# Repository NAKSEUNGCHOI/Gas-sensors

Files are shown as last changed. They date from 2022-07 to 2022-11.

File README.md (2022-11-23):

# Project Gas(Air quality) sensors

* University of Washington Summer 2022 
* Prof. Vikram Iyer.
* Nakseung Choi | graduate research assistant @ SSOL UW 

## Description

* Prof. Vikram Iyer and I are currently building low power low cost gas sensors (CO2, CO, and black carbon) to help two groups of scientists collect data for their research studies. One group wants to get data in the greater Seattle area to study on where these gasses are coming from. Ultimately, they would like to expand the number of the gas sensors in different locations such that they can compare with other locations for further studies.
The other group would like to place these gas sensors in the middle of moutains in the eastern Washington to study how these gases(CO2 and CO) affect wild animals when there is an unexpected wildfire going. 

* We are currently testing several CO2 sensors to compare their functionality with a commercial device. In the mean time, we just got done with our own PCB design for SPEC CO sensor as well as hardware/software integration. Depending on how precise data the scientists need, we are going to make it acordingly. nRF52480 Arm Cortex-m4 is probably going to be used for the MCU. Using Lora radio communication, a long distance communication interface will also be implemented to update data to the web server such that the scientists can check the data in real time.  

## Authors

- Nakseung Choi
- Please check out my Linkedin: https://www.linkedin.com/in/nakseung-choi-090a1b69/

## Release Notes

* <pre> New Tube arrived. About to go install the MA350 on the rooftop                       11-22-2022</pre>
* <pre> 300ml/min 60 ml/min for 5 wavelengths tests are done. missing 60 ml/min with UV+IR    9-12-2022</pre>
* <pre> Created another python code to draw different plots for CO2 sensors                   9-12-2022</pre>
* <pre> Wrote a python code to plot CO2 sensors - avg of two aranets for 4 sensors            9-08-2022</pre>
* <pre> wrote a python program using mathplot to graph the CO2 data  (Still testing MA350)    9-07-2022</pre>
* <pre> Testing the MA350                                                                     8-29-2022</pre>
* <pre> arduino / python serial communication script complete. Sending data to adafruitIO     8-26-2022</pre>
* <pre> presentation done. more CO testing / preparing to set up MA350.                       8-24-2022</pre>                                                
* <pre> got the CO sensor working with noise. more testing...........                         8-23-2022</pre>
* <pre> created a new PCB board and testing..                                                 8-22-2022</pre>
* <pre> presentation preparation2                                                             8-20-2022</pre>
* <pre> presentation preparation                                                              8-20-2022</pre>
* <pre> Software done. software/hardware integration started                                  8-18-2022</pre>
* <pre> Testing CO sensor 2                                                                   8-17-2022</pre>
* <pre> Testing CO sensor                                                                     8-16-2022</pre>
* <pre> setting up Black Carbon sensor & CO sensor                                            8-15-2022</pre>
* <pre> testing two SCD41s, two aranets, two PASCO2s all together.                            8-15-2022</pre>
* <pre>Debugging Complete. Ready to go for a testing.                                         8-14-2022</pre>
* <pre>Debugging...                                                                           8-12-2022</pre>
* <pre>PASCO2s are going to be tested with scd41 and aranet4 together for the functionality   8-11-2022</pre>
* <pre>Xensiv PAS CO2 coding in python complete.                                              8-11-2022</pre>
* <pre>Xensiv PAS CO2 working. Testing started.                                               8-10-2022</pre>
* <pre>Debugging Xensiv PAS CO2                                                               8-09-2022</pre>
* <pre>Testing Xensiv PAS CO2 manufactured by Infineon.                                       8-08-2022</pre>
* <pre>All parts are done soldering onto the board. Going to test the PCB.                    8-07-2022</pre>
* <pre>CO sensor PCB design complete. About to sorder the CO sensor circuit.                  8-03-2022</pre> 
* <pre>Designing a new circuit for CO sensor due to the chip shortage (LMP9100 out of stock)  8-02-2022</pre>
* <pre>Installed CO2 sensor's in an office with two people.                                   7-28-2022</pre>
* <pre>CO Sensor PCB Design V2 complete.                                                      7-28-2022</pre>
* <pre>CO Sensor PCB Design complete.                                                         7-27-2022</pre>
* <pre>Testing 24 hours success.                                                              7-26-2022</pre>
* <pre>Testing two SCD41s and two aranets4s on Raspberry pi 3.                                7-25-2022</pre>
* <pre>Working on PCB design for CO sensor                                                    7-24-2022</pre>
* <pre>Implemented two SCD41s and two aranet4s on Raspberry pi 3 for a testing.               7-21-2022</pre>
* <pre>Implemented SCD41 on nRF52480 express with Lora Radio (RFM9x)                          7-07-2022</pre>
* <pre>Implemented SCD41 (via I2C) and Aranet4 (via Bluetooth) on Raspberry pi 3 (B type)     7-01-2022</pre>
* <pre>Started                                                                                6/24/2022</pre>

## License

Copyright @ Nakseung Choi.

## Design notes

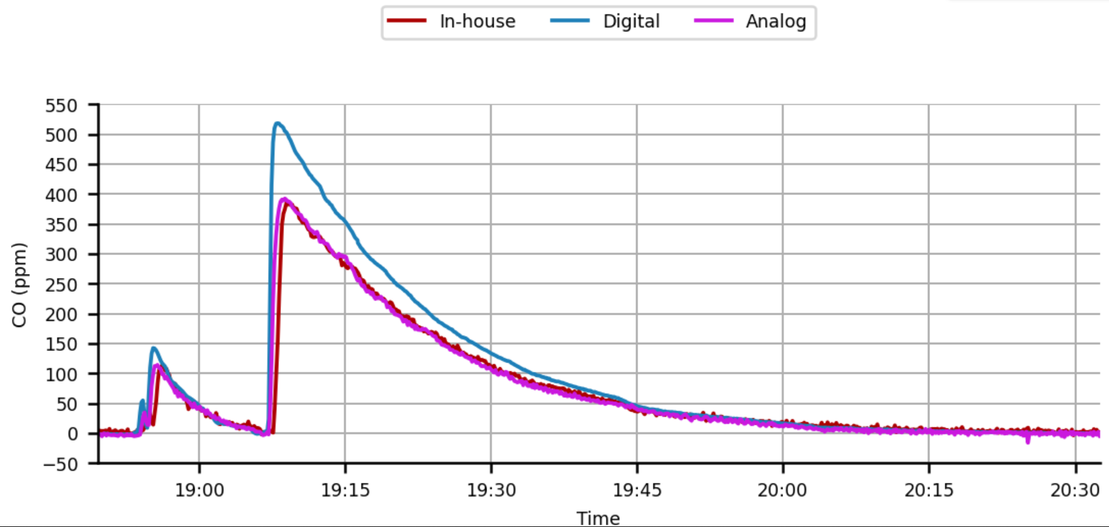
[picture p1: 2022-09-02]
CO/plot/CO_plot1.png

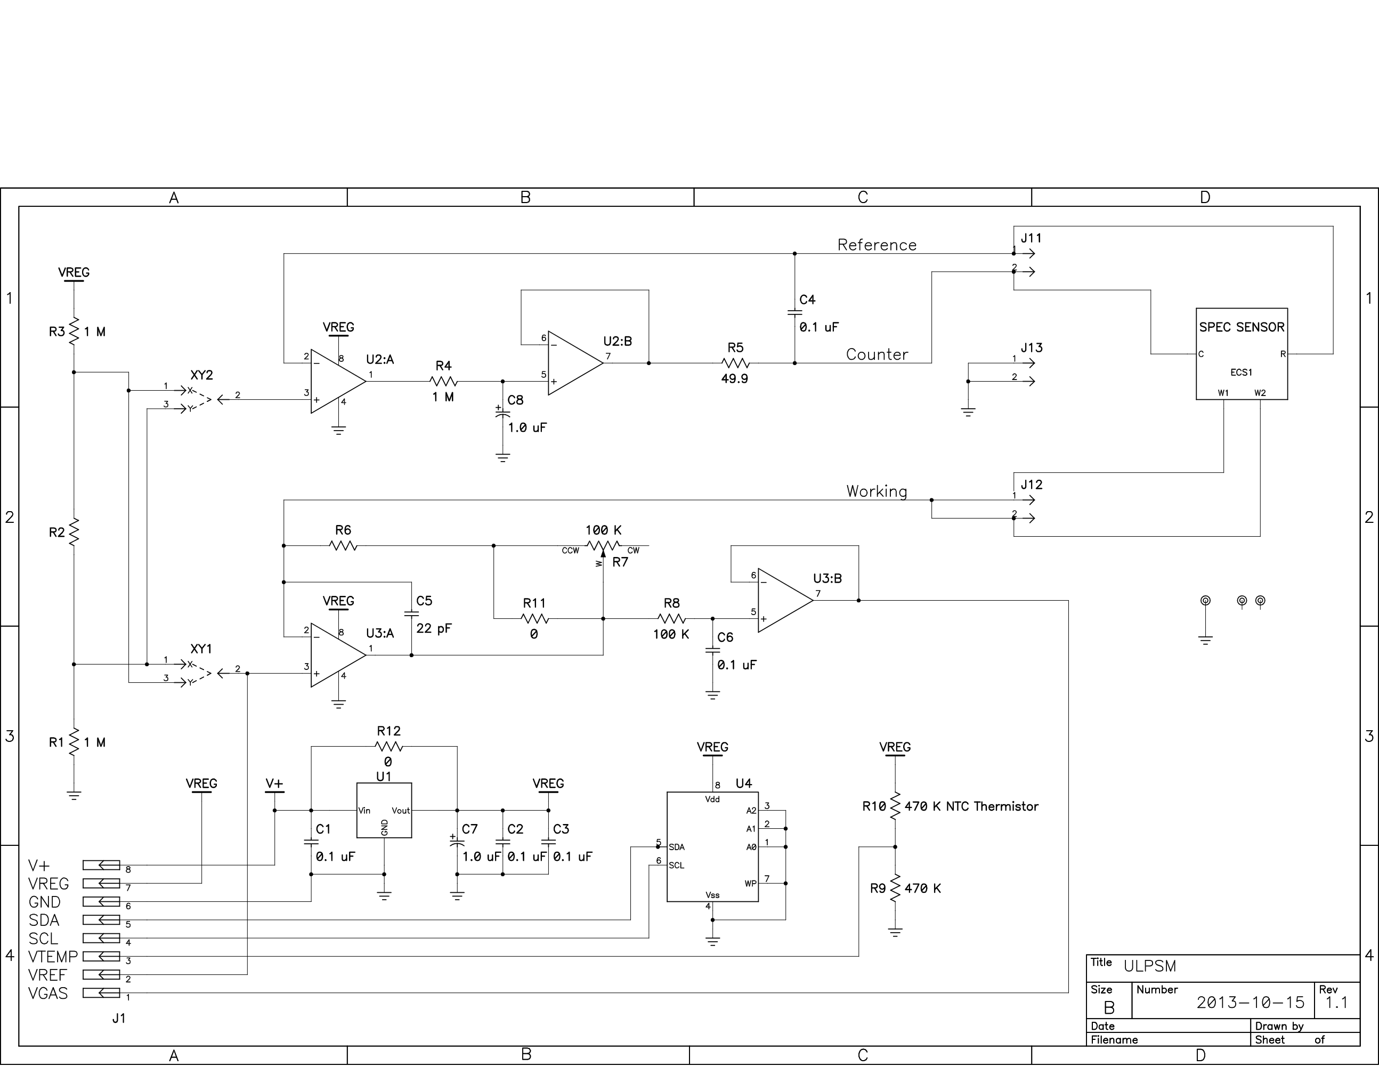
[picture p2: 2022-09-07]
CO/download.png

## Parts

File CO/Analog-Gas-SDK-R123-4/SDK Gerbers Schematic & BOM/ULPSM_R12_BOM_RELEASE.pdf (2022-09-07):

Bill of Materials | ULPSM Rev. 1.2
ULPSM | BOM Rev. 1.1
Item | Ref. Des. | # Req | Mfr.'s Part No. | Notes
Circuit Board | | 1 | ULPSM_R12
Connector, 8 pin female | J1 | 1 | Sullins PPPC081LGBN-RC
Capacitor, Ceramic, 0.1uF 25V SMT0805 | C1-4, 6 | 1 | Kemet C0805C104K3RACTU
Capacitor, Ceramic, 22pF 50V SMT0805 | C5 | 1 | Kemet C0805C220K5GACTU
Capacitor, Ceramic, 1.0uF 25V SMT0805 | C7,8 | 2 | F951E105MPAAQ2
Resistor, 0.0 SMT0603 | BIAS +/- | 2 | Yageo RC0603JR-070RL | See ULPSM_R12 SETTINGS_TABLE
Resistor, 0.0 SMT0805 | R11,R12 | 2 | Yageo RC0805JR-070RL
Resistor, 1M 1% SMT0805 | R1,3,4 | 3 | Yageo RC0805FR-071ML
Resistor, Variable Value, 1% SMT0805 | R2 | 1 | Variable Value | See ULPSM_R12 SETTINGS_TABLE
Resistor, 49.9 1% SMT0805 | R5 | 1 | Yageo RC0805FR-0749R9L
Resistor, Variable Value, 1% SMT0805 | R6 | 1 | Variable Value | See ULPSM_R12 SETTINGS_TABLE
Resistor, 100K 1% SMT0805 | R8 | 1 | Yageo RC0805FR-07100KL
Amplifier, dual, MSOP-8 pkg. | U2,U3 | 2 | Microchip MCP6042T-I/MS
Thermistor, 470K 5% NTC SMT0603 | R10 | 1 | MuRata NCP18WM474J03RB
Resistor, 470K 1% SMT0603 | R9 | 1 | Yageo RC0603FR-07470KL
Connector, 2 pin, female | J11-13 | 3 | 3M 950502-6102-AR
Captive Fastener/Standoff | HOLE | 1 | Captive Fastener CKFSE-116-4
IC, EEPROM, 16KBIT, MSOP-8 | U4 | 1 | Microchip 24AA16-I/MS | DNI
Voltage Regulator, 3V, SOT-23-5 | U1 | 1 | Seiko S-812C30AMC-C2KT2G | DNI
Potentiometer, 100K | R7 | 1 | Copal ST4ETB104 | DNI

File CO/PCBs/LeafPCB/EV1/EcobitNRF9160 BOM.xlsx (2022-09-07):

Column1 | Column2 | Column3 | Column4 | Column5 | Column6 | Column7 | Column8 | Column9
Part | Value | Device | Package | Description
BATT | 3-6VDC | CON_JST_PH_2PIN | JSTPH2 | JST 2-Pin Right-Angle Connector | https://www.digikey.com/product-detail/en/jst-sales-america-inc/S2B-PH-SM4-TB(LF)(SN)/455-1749-1-ND/926846 | 0.4194 | 1 | 0.4194
C1 | 10uF | CAP0402 | C-0402 | CAP | https://www.digikey.com/product-detail/en/murata-electronics-north-america/GRM155R60G106ME44D/490-10693-1-ND/5251412 | 0.011 | 1 | 0.011
C2, C3, C4, C5 | 1uF | CAPACITOR_0402_N | RESC0402_N | Generic chip capacitor | https://www.digikey.com/product-detail/en/samsung-electro-mechanics/CL05A105MQ5NNNC/1276-1235-1-ND/3889321 | 0.073 | 4 | 0.292
CHG |  | LED0805_NOOUTLINE | CHIPLED_0805_NOOUTLINE | LED | https://www.digikey.com/product-detail/en/lite-on-inc/LTST-C170AKT/160-1177-6-ND/1888608 | 0.1462 | 1 | 0.1462
JP1 | USB-RECEPTABLE | USB-RECEPTABLE | FCI-10103594-0001LF | USB Receptable | https://www.digikey.com/product-detail/en/amphenol-icc-fci/10103594-0001LF/609-4050-1-ND/2350357 | 0.5982 | 1 | 0.5982
L1 | 22nH | INDUCTOR_0603_N | RESC0603_N | Generic chip inductor | https://www.digikey.com/product-detail/en/johanson-technology-inc/L-14C22NJV4T/712-1438-1-ND/1914888 | 0.0438 | 1 | 0.0438
P1 | SF72S006VBAR2500 | SF72S006VBAR2500 | JAE_SF72S006VBAR2500 | SF72 series, nano-SIM card connector, normail open type, 6 connector | https://www.digikey.com/product-detail/en/SF72S006VBAR2500/670-2799-1-ND/5247732/?itemSeq=285035164 | 1.62 | 1 | 1.62
Q1 | Btn | SWITCH_TACT_SMT4.6X2.8 | BTN_KMR2_4.6X2.8 | SMT Tact Switches | https://www.digikey.com/product-detail/en/c-k/KMR231NG-LFS/CKN10246CT-ND/2176497 | 0.4065 | 1 | 0.4065
R1, R2, R4, R5, R6, R7 | 10k | RESR0402 | R0402 | RES | https://www.digikey.com/product-detail/en/susumu/RR0510P-103-D/RR05P10.0KDCT-ND/432960 | 0.0299 | 6 | 0.1794
R3 | 1k | RESR0402 | R0402 | RES | https://www.digikey.com/product-detail/en/susumu/RR0510P-102-D/RR05P1.0KDCT-ND/432937 | 0.0299 | 1 | 0.0299
THERM | 10k | RESISTOR_0402 | _0402 | Resistors | https://www.digikey.com/product-detail/en/susumu/RR0510P-103-D/RR05P10.0KDCT-ND/432960 | 0.0299 | 1 | 0.0299
U1 | ALS-PT19-315C | LIGHT_ALS-PT19-315C | ALS-PT19-315C | ALS-PT19-315C - Analog Light Sensor | https://www.digikey.com/product-detail/en/everlight-electronics-co-ltd/ALS-PT19-315C-L177-TR8/1080-1244-1-ND/2675978 | 0.2297 | 1 | 0.2297
U2 | NCP718 | NCP718 | NCP718-WDFN6 |  | https://www.digikey.com/product-detail/en/on-semiconductor/NCP718AMTADJTBG/NCP718AMTADJTBGOSCT-ND/9169230 | 0.3909 | 1 | 0.3909
U3 | MCP73831T-2ACI/OT | MCP73831/2 | SOT23-5 | MCP73831/2 LIPO Charger | https://www.digikey.com/product-detail/en/microchip-technology/MCP73831T-2ACI-OT/MCP73831T-2ACI-OTCT-ND/1979802 | 0.4326 | 1 | 0.4326
U4 | AP3418 | AP3418 | SOT25 |  | https://www.digikey.com/product-detail/en/diodes-incorporated/AP3418KTR-G1/AP3418KTR-G1DICT-ND/4505309 | 0.3399 | 1 | 0.3399
U5 | TPS22860DBVR | TPS22860DBVR | R-PDSO-G6 | Power Switch ICs - Power Distribution TPS22860 Ultra-low leakage load switch 6-SOT-23 -40 to 85 | https://www.digikey.com/product-detail/en/texas-instruments/TPS22860DBVR/296-43982-1-ND/5973206 | 0.5828 | 1 | 0.5828
 |  |  |  |  |  |  |  | 5.7522

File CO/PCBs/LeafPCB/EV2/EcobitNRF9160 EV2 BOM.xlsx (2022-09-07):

Column1 | Column2 | Column3 | Column4
Part | Value | Device | Package
ADC-CO | LMP91000SD/NOPB | LMP91000SD/NOPB | SON50P400X400X80-15N
ADC-NO2 | LMP91000SD/NOPB | LMP91000SD/NOPB | SON50P400X400X80-15N
ADC-O3 | LMP91000SD/NOPB | LMP91000SD/NOPB | SON50P400X400X80-15N
ADC-SO2 | LMP91000SD/NOPB | LMP91000SD/NOPB | SON50P400X400X80-15N
BATT | 3-6VDC | CON_JST_PH_2PIN | JSTPH2
C1 | 10uF | CAP0402 | C-0402
C2, C3, C4, C5, C6 | 1uF | CAPACITOR_0402_N | RESC0402_N
C7 | 10uF 10V 20% Tant | CAPACITOR_0805_N | RESC0805_N
C10, C11, C20, C30, C40 | 0.1uF | CAPACITOR_0603_N | RESC0603_N
CHG |  | LED0805_NOOUTLINE | CHIPLED_0805_NOOUTLINE
IC1 | ISL60002DIH320Z-TK | ISL60002DIH320Z-TK | SOT-23-3
JP1 | USB-RECEPTABLE | USB-RECEPTABLE | FCI-10103594-0001LF
L1 | 22nH | INDUCTOR_0603_N | RESC0603_N
P1 | SF72S006VBAR2500 | SF72S006VBAR2500 | JAE_SF72S006VBAR2500
Q1 | Btn | SWITCH_TACT_SMT4.6X2.8 | BTN_KMR2_4.6X2.8
R1, R4, R5, R6 | 10k | RESR0402 | R0402
R2 | 2M | R-US_R0603 | R0603
R3, R7 | 1k | RESR0402 | R0402
R11, R21, R31, R41 | 499k | RESISTOR_0603_N | RESC0603_N
R8 | 806k | R-US_R0603 | R0603
R10, R20, R30, R40 | 49.9k | RESISTOR_0603_N | RESC0603_N
IC2 | HDC1080 | HDC1080 | TI-S-PWSON-N6
U1 | VEML7700-TR | VEML7700-TR | XDCR_VEML7700-TR
U2 | NCP718 | NCP718 | NCP718-WDFN6
U3 | MCP73831T-2ACI/OT | MCP73831/2 | SOT23-5
U4 | AP3418 | AP3418 | SOT25
U5 | TPS22860DBVR | TPS22860DBVR | R-PDSO-G6
U6 | MCP6041T-I/OT

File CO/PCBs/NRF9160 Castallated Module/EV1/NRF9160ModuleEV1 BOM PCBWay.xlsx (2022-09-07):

Column1 | Column2 | Column3 | Column4 | Column5 | Column6
Part | Value | Device | Package | Description | Part
C1, C2, C3, C4 | 4.7uF | CAP0402 | C-0402 | CAP | https://www.digikey.com/product-detail/en/murata-electronics-north-america/GRM155R60J475ME47D/490-5915-1-ND/3719860
C5 | 3.5pF | CAPACITOR_0402_N | RESC0402_N | Generic chip capacitor | https://www.digikey.com/product-detail/en/kemet/CBR04C359B5GAC/399-16078-1-ND/7649663
IC1 | NRF9160 | NRF9160 | NRF9160 |  | https://www.mouser.com/ProductDetail/Nordic-Semiconductor/nRF9160-SICA-R
L1 | 1.5nH | INDUCTOR_0603_N | RESC0603_N | Generic chip inductor | https://www.digikey.com/product-detail/en/johanson-technology-inc/L-14C1N5SV4T/712-1425-1-ND/1914875
L2 | 22nH | INDUCTOR_0603_N | RESC0603_N | Generic chip inductor | https://www.digikey.com/product-detail/en/johanson-technology-inc/L-14C22NJV4T/712-1438-1-ND/1914888
LED | Blue | LED0603 | LED-0603 | LED (Generic) | https://www.digikey.com/product-detail/en/osram-opto-semiconductors-inc/LB-Q39G-L2OO-35-1/475-2816-1-ND/2176355
R1, R8 | 1k | RESR0402 | R0402 | RES | https://www.digikey.com/product-detail/en/susumu/RR0510P-102-D/RR05P1.0KDCT-ND/432937
U1 | TPD3F303 | TPD3F303 | 8-UFDFN |  | https://www.digikey.com/product-detail/en/texas-instruments/TPD3F303DQDR/296-28300-1-ND/2605062
U2 | MM8130-2600 | MM8130-2600 | MM8130-2600 |  | https://www.digikey.com/product-detail/en/murata-electronics-north-america/MM8130-2600RB8/490-8450-1-ND/4380750

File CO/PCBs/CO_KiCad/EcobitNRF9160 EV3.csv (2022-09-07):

Source: | C:\Users\chlsk\OneDrive\Desktop\PCBs\CO_KiCad\EcobitNRF9160 EV3.kicad_sch
Date: | 7/28/2022 14:46
Tool: | Eeschema (6.0.6)
Generator: | C:\Program Files\KiCad\6.0\bin\scripting\plugins/bom_csv_grouped_by_value_with_fp.py
Component Count: | 11
Ref | Qnty | Value | Cmp name | Footprint | Description | Vendor
AFE-CO1, | 1 | LMP91000SD/NOPB | LMP91000SD{slash}NOPB | EcobitNRF9160 EV3:SON50P400X400X80-15N
AMP-CO1, | 1 | MCP6041T-E/OT | MCP6041T-E{slash}OT | EcobitNRF9160 EV3:SOT95P320X145-5N
C1, | 1 | 10uF 10V 20% Tant | CAPACITOR_0805_N | EcobitNRF9160 EV3:RESC0805_N
C2, C3, | 2 | 0.1uF | CAPACITOR_0603_N | EcobitNRF9160 EV3:RESC0603_N
IC1, | 1 | ISL60002DIH320Z-TK | ISL60002DIH320Z-TK | EcobitNRF9160 EV3:SOT-23-3
J1, | 1 | Conn_01x06_Male | Conn_01x06_Male | Connector_PinSocket_2.54mm:PinSocket_1x06_P2.54mm_Vertical | Generic connector, single row, 01x06, script generated (kicad-library-utils/schlib/autogen/connector/)
R1, R2, | 2 | 499k | RESISTOR_0603_N | EcobitNRF9160 EV3:RESC0603_N
R3, | 1 | 1k | RESISTOR_0603_N | EcobitNRF9160 EV3:RESC0603_N
SENS-CO1, | 1 | SPECSENSOR | SPECSENSOR | Libraries:3SP_CO_1000_P_Package_2

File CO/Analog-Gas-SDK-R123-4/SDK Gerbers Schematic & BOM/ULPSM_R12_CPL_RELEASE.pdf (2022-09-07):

Page 1 of 1

======================================================================

Report | Origin | = | (0.0, | 0.0)
Units | used | = | mil
RefDes | Layer | LocationX | LocationY | Rotation | Fixed
‐‐‐‐‐‐‐‐‐‐‐‐‐‐‐ | ‐‐‐‐‐‐‐‐‐‐‐‐‐‐‐ | ‐‐‐‐‐‐‐‐‐‐ | ‐‐‐‐‐‐‐‐‐‐ | ‐‐‐‐‐‐‐‐ | ‐‐‐‐‐
C1 | Bottom | 1850.0 | 1650.0 | 90.0 | Yes
C2 | Bottom | 1650.0 | 1450.0 | 90.0 | Yes
C3 | Bottom | 2150.0 | 1625.0 | 270.0 | Yes
C4 | Bottom | 1450.0 | 1650.0 | 270.0 | Yes
C5 | Bottom | 2150.0 | 1200.0 | 270.0 | Yes
C6 | Bottom | 1750.0 | 1450.0 | 90.0 | Yes
C7 | Bottom | 1750.0 | 1650.0 | 270.0 | Yes
C8 | Bottom | 1850.0 | 1200.0 | 90.0 | Yes
J1 | Bottom | 2350.0 | 1410.0 | 90.0 | Yes
J11 | Top | 1450.0 | 1410.0 | 90.0 | Yes
J12 | Top | 2150.0 | 1410.0 | 270.0 | Yes
J13 | Top | 1800.0 | 1060.0 | 180.0 | Yes
R1 | Bottom | 1100.0 | 1700.0 | 90.0 | Yes
R2 | Bottom | 1200.0 | 1700.0 | 270.0 | Yes
R3 | Bottom | 1300.0 | 1700.0 | 90.0 | Yes
R4 | Bottom | 1750.0 | 1200.0 | 270.0 | Yes
R5 | Bottom | 1550.0 | 1450.0 | 270.0 | Yes
R6 | Bottom | 2250.0 | 1400.0 | 90.0 | Yes
R7 | Top | 2600.0 | 1200.0 | 180.0 | Yes
R8 | Bottom | 1850.0 | 1450.0 | 90.0 | Yes
R9 | Top | 2500.0 | 1500.0 | 90.0 | Yes
R10 | Top | 2600.0 | 1500.0 | 270.0 | Yes
R11 | Bottom | 2250.0 | 1200.0 | 90.0 | Yes
R12 | Top | 2590.0 | 1700.0 | 90.0 | Yes
TP1 | Top | 1800.0 | 1770.0 | 0.0 | Yes
TP2 | Top | 1435.0 | 1775.0 | 0.0 | Yes
TP3 | Top | 2165.0 | 1045.0 | 0.0 | Yes
U1 | Bottom | 1590.0 | 1640.0 | 270.0 | Yes
U2 | Bottom | 1650.0 | 1100.0 | 0.0 | Yes
U3 | Bottom | 2025.0 | 1100.0 | 0.0 | Yes
U4 | Bottom | 2025.0 | 1450.0 | 0.0 | Yes
XY1 | Top | 1200.0 | 1150.0 | 0.0 | Yes
XY2 | Top | 1200.0 | 1050.0 | 0.0 | Yes
Qty | = | 33

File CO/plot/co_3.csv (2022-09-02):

id | value | feed_id | created_at | lat | lon | ele
0F3JCV4WYZSHBMRVRRGGXMJQK9 | -1.83 | 2307251 | 2022-08-26 22:00:11 UTC
0F3JCV7K7EMJ0QWT7HCGX4BCGC | -1.00 | 2307251 | 2022-08-26 22:00:19 UTC
0F3JCVAA159DK7FD22NXF3T5PT | -0.10 | 2307251 | 2022-08-26 22:00:28 UTC
0F3JCVD6GWJ9M95N14SA5GFM5M | 2.82 | 2307251 | 2022-08-26 22:00:38 UTC
0F3JCVFR802YP4HFEQQ4X7B2K7 | -1.15 | 2307251 | 2022-08-26 22:00:46 UTC
0F3JCVJRZ1PP207812ACC8YJ78 | -2.38 | 2307251 | 2022-08-26 22:00:56 UTC
0F3JCVNFXS5SMDS7W42DMZHYVY | -1.00 | 2307251 | 2022-08-26 22:01:05 UTC
0F3JCVR7AFP769AHVT937V24Z9 | 0.81 | 2307251 | 2022-08-26 22:01:14 UTC
0F3JCVTY8VHTMH4JNDVCJPYXD1 | 1.65 | 2307251 | 2022-08-26 22:01:23 UTC
0F3JCVXMVE6XFJNGMAMNYVMV7N | 1.51 | 2307251 | 2022-08-26 22:01:32 UTC
0F3JCW0CHE90W8FHG998KPV5FV | 3.68 | 2307251 | 2022-08-26 22:01:41 UTC
0F3JCW32QE673M2HQX39NVNSZ6 | 0.01 | 2307251 | 2022-08-26 22:01:49 UTC
0F3JCW5T1KKKW1PQ45RJ6TC0EJ | 0.01 | 2307251 | 2022-08-26 22:01:58 UTC
0F3JCW8H5QYJ19QF6D1H9PSP70 | 0.93 | 2307251 | 2022-08-26 22:02:07 UTC
0F3JCWB85W4N37N8P42M68G058 | -1.39 | 2307251 | 2022-08-26 22:02:16 UTC
0F3JCWE9BMSA7FVASXYGPB9FSF | -2.44 | 2307251 | 2022-08-26 22:02:26 UTC
0F3JCWHAYXW3365ATW7K02Q6VZ | 1.89 | 2307251 | 2022-08-26 22:02:36 UTC
0F3JCWKQG8G0T9TTGC0BA4ABT9 | -0.01 | 2307251 | 2022-08-26 22:02:44 UTC
0F3JCWPDXHAHFEWF0R2A9XEGSQ | 2.55 | 2307251 | 2022-08-26 22:02:53 UTC
0F3JCWS4MDERT1GH2J4X1B8KD8 | -1.74 | 2307251 | 2022-08-26 22:03:02 UTC
0F3JCWVVDXYBZFFX2CHAA7B0YN | -0.72 | 2307251 | 2022-08-26 22:03:11 UTC
0F3JCWYJGBHBA8XE7NXGYBW9TT | -1.03 | 2307251 | 2022-08-26 22:03:19 UTC
0F3JCX19V61TDZPQBG0G76QV39 | 1.04 | 2307251 | 2022-08-26 22:03:28 UTC
0F3JCX47RR36NS1ZCYS2TS78T0 | 2.66 | 2307251 | 2022-08-26 22:03:38 UTC
0F3JCX714S9379WKT0WMCM72V9 | 5.37 | 2307251 | 2022-08-26 22:03:47 UTC
0F3JCX9R325P56B4AD3KKYC69C | -1.65 | 2307251 | 2022-08-26 22:03:56 UTC
0F3JCXCFEDC2CVV9YB3FTZV57W | -0.47 | 2307251 | 2022-08-26 22:04:05 UTC
0F3JCXF6R8GJFKD42Y6V91Y9ME | 1.40 | 2307251 | 2022-08-26 22:04:14 UTC
0F3JCXHX0QBPBYGTNTTMQYGJP7 | 2.94 | 2307251 | 2022-08-26 22:04:23 UTC
0F3JCXMM3WKN73ZXA3BP8G7TN7 | 0.49 | 2307251 | 2022-08-26 22:04:32 UTC
0F3JCXQAYQ67TAK3P6D590R929 | 1.69 | 2307251 | 2022-08-26 22:04:41 UTC
0F3JCXT1Z176EAGH4G7FC0Q9MR | 1.36 | 2307251 | 2022-08-26 22:04:50 UTC
0F3JCXWRQ484N4NAZJA5AYM21Q | -0.25 | 2307251 | 2022-08-26 22:04:58 UTC
0F3JCXZT1SVHA2GDDZ0VDDG34M | 0.52 | 2307251 | 2022-08-26 22:05:08 UTC
0F3JCY2GW1ZEN47DN5DKT32DXJ | -3.31 | 2307251 | 2022-08-26 22:05:17 UTC
0F3JCY57SYH0H8XE3M3M4FNNXS | 2.78 | 2307251 | 2022-08-26 22:05:26 UTC
0F3JCY7YH7V3JYCKBS3J7JTJGC | 3.45 | 2307251 | 2022-08-26 22:05:35 UTC
0F3JCYANP242M73JT6H6WNN2MG | 4.11 | 2307251 | 2022-08-26 22:05:44 UTC
0F3JCYDCQB9XZDW60CPP4TBP6R | 2.25 | 2307251 | 2022-08-26 22:05:53 UTC
0F3JCYG3JB3D2GYGNEDB60RFVX | -2.03 | 2307251 | 2022-08-26 22:06:02 UTC
0F3JCYJTMBVE3C8THWNQ3EMBVP | 1.21 | 2307251 | 2022-08-26 22:06:11 UTC
0F3JCYNHVWV8YV32AMG6PDB83P | -2.39 | 2307251 | 2022-08-26 22:06:20 UTC
0F3JCYRHS86VGCW9Q0BQF16V63 | -3.33 | 2307251 | 2022-08-26 22:06:29 UTC
0F3JCYVH56RRDCXX5A077Q90PM | 3.23 | 2307251 | 2022-08-26 22:06:39 UTC
0F3JCYXZY9DTE9PWYJ8AV6K9GM | 5.32 | 2307251 | 2022-08-26 22:06:47 UTC
0F3JCZ0QBK0BSGBEAZD706TWJ8 | -3.22 | 2307251 | 2022-08-26 22:06:56 UTC
0F3JCZ3HZ25ZGGWCDCXRFHBV8B | -0.06 | 2307251 | 2022-08-26 22:07:06 UTC
0F3JCZ692JX8FMP7GPQ4NCJ4RS | 2.29 | 2307251 | 2022-08-26 22:07:14 UTC
0F3JCZ8XWA7MX0XCE82BBRFHHM | -0.35 | 2307251 | 2022-08-26 22:07:23 UTC
0F3JCZBP2JZSZ7Z0MK7M1SQQJE | -1.33 | 2307251 | 2022-08-26 22:07:32 UTC
0F3JCZEBREED1RJZQFTG3ZFWW2 | 0.33 | 2307251 | 2022-08-26 22:07:41 UTC
0F3JCZH5Y2HC62RTG15K5Y2VDE | 4.45 | 2307251 | 2022-08-26 22:07:50 UTC
0F3JCZM6GDPC2YFN0G6893SCKE | 2.79 | 2307251 | 2022-08-26 22:08:00 UTC
0F3JCZPWADTNZYGVCTH9A3T8Y2 | 5.61 | 2307251 | 2022-08-26 22:08:09 UTC
0F3JCZSMJH95CEVVMG3QPTSP2Z | -1.39 | 2307251 | 2022-08-26 22:08:18 UTC
0F3JCZWD40JNWCHCBH3Q2TM7QQ | -2.67 | 2307251 | 2022-08-26 22:08:27 UTC
0F3JCZZ9JF39Q3XFNMVBFBAW9M | 5.86 | 2307251 | 2022-08-26 22:08:36 UTC
0F3JD01RY5419QWNYZ8C04B65F | 1.84 | 2307251 | 2022-08-26 22:08:45 UTC
0F3JD04HWHEY5RCAYCPRT4WG6G | 1.40 | 2307251 | 2022-08-26 22:08:54 UTC
0F3JD079QF61F711N5R5890KE9 | 2.82 | 2307251 | 2022-08-26 22:09:03 UTC
0F3JD09XYKNT41C91VFZA5TCPA | 4.85 | 2307251 | 2022-08-26 22:09:11 UTC
0F3JD0CVG6YGGZMM2M18GJ1WCQ | 1.40 | 2307251 | 2022-08-26 22:09:21 UTC
0F3JD0FGK9G2E2V1KENAXNRXWY | -0.80 | 2307251 | 2022-08-26 22:09:30 UTC
0F3JD0JH0GYWAMN8KKEBGWBW28 | 2.03 | 2307251 | 2022-08-26 22:09:39 UTC
0F3JD0MZBZXTS2H3ZZS0AHQFYM | 1.82 | 2307251 | 2022-08-26 22:09:47 UTC
0F3JD0QNVHEY971YXNGAE83X9D | 0.41 | 2307251 | 2022-08-26 22:09:56 UTC
0F3JD0TCV2BQ2CME9VMDA6XTC4 | -3.24 | 2307251 | 2022-08-26 22:10:05 UTC
0F3JD0X38V2SBFDMCM0QGQ2731 | 0.81 | 2307251 | 2022-08-26 22:10:14 UTC
0F3JD0ZTGD2FDARQABKJ80QTWG | -1.97 | 2307251 | 2022-08-26 22:10:23 UTC
0F3JD12HY2CZSGC88VZKH770G1 | 1.40 | 2307251 | 2022-08-26 22:10:32 UTC
0F3JD15J6KWFC9YJRJ39175KZR | -0.44 | 2307251 | 2022-08-26 22:10:42 UTC
0F3JD189AWVM2S9DS6ZGB6PV0N | 2.33 | 2307251 | 2022-08-26 22:10:51 UTC
0F3JD1B0BP3R905SQT0GK7CT3T | 0.64 | 2307251 | 2022-08-26 22:11:00 UTC
0F3JD1DQ5ASPWT5CNWEQ8BCCZF | 1.40 | 2307251 | 2022-08-26 22:11:09 UTC
0F3JD1HYVSPNYGVADSD17A5BFD | -144.78 | 2307251 | 2022-08-26 22:11:22 UTC
0F3JD1K4HQ75024S4WRKNYNJD8 | -47.14 | 2307251 | 2022-08-26 22:11:26 UTC
0F3JD1NW3N120G51GF7A2Q85T3 | 112.80 | 2307251 | 2022-08-26 22:11:35 UTC
0F3JD1T3PZC7YGNAF68PHZH48T | -222.44 | 2307251 | 2022-08-26 22:11:49 UTC
0F3JD1V9S41THBE4DBC93D6GSD | 154.43 | 2307251 | 2022-08-26 22:11:53 UTC
0F3JD211TQF9JQKDRB4JH0ARPX | -64.73 | 2307251 | 2022-08-26 22:12:12 UTC
0F3JD23R9EKNMN3YECPDGCTJBW | 33.66 | 2307251 | 2022-08-26 22:12:21 UTC
0F3JD29CKS2E5TTN8QW79V7QNF | 20.58 | 2307251 | 2022-08-26 22:12:39 UTC
0F3JD2BWWXW4GBXSNH1J8GW1WP | -0.29 | 2307251 | 2022-08-26 22:12:47 UTC
0F3JD2EM48Z1MGC56ZY44R418R | 6.09 | 2307251 | 2022-08-26 22:12:56 UTC
0F3JD2HE0HB9Y1EZBPR9Q0D4DK | 0.33 | 2307251 | 2022-08-26 22:13:06 UTC
0F3JD2M27M190WZJ2J06QCJ8R9 | 0.94 | 2307251 | 2022-08-26 22:13:14 UTC
0F3JD2Q2PFGHBN1PQ8XR7CYBRK | 2.74 | 2307251 | 2022-08-26 22:13:24 UTC
0F3JD2SSGH614P34NDMSXV3XHP | -3.23 | 2307251 | 2022-08-26 22:13:33 UTC
0F3JD2WGG639PF1TGB5P74CWHE | -0.60 | 2307251 | 2022-08-26 22:13:42 UTC
0F3JD37CR3SC1PX7DAFWY27RVY | -4.33 | 2307251 | 2022-08-26 22:14:18 UTC
0F3JD3A2V6X7A74F9VBSYXWTCN | 4.09 | 2307251 | 2022-08-26 22:14:26 UTC
0F3JD3CT75V3V4N23HTTX465YB | 1.76 | 2307251 | 2022-08-26 22:14:35 UTC
0F3JD3FTXE53KBZ85HVM1WJQMW | 1.86 | 2307251 | 2022-08-26 22:14:45 UTC
0F3JD3JHKTDKXZAZV2SA35GKMN | -1.91 | 2307251 | 2022-08-26 22:14:54 UTC
0F3JD3N9EB6M834VNHCG6D4JW1 | 1.89 | 2307251 | 2022-08-26 22:15:03 UTC
0F3JD3QZMJ3XXHKEYYTDY9JSRF | -3.60 | 2307251 | 2022-08-26 22:15:12 UTC
0F3JD3TPCBPTG3VJE19VM8Z1MZ | 3.43 | 2307251 | 2022-08-26 22:15:21 UTC
0F3JD3XDETF3032GC611JMJ9S0 | -1.17 | 2307251 | 2022-08-26 22:15:30 UTC
0F3JD40C3T6AMWQ22B97HMANH0 | 3.16 | 2307251 | 2022-08-26 22:15:39 UTC
0F3JD42V3V6JF4BERDMGV08TP5 | 2.97 | 2307251 | 2022-08-26 22:15:47 UTC
0F3JD45J0KVPSVATHCJWNPWM17 | 0.75 | 2307251 | 2022-08-26 22:15:56 UTC
0F3JD48JKV0JEDC2NGV1SJTEEZ | 0.01 | 2307251 | 2022-08-26 22:16:06 UTC
0F3JD4B97NWM4X0V8K9AGH5BJ6 | -4.41 | 2307251 | 2022-08-26 22:16:15 UTC
0F3JD4E107S9ZVGPZB0EFPCFR4 | 7.10 | 2307251 | 2022-08-26 22:16:24 UTC
0F3JD4GQ8SX1RNGQBEWZKHQKPQ | 1.08 | 2307251 | 2022-08-26 22:16:33 UTC
0F3JD4KEMN5QGK5AW0X4DCK86A | -1.18 | 2307251 | 2022-08-26 22:16:42 UTC
0F3JD4P5SHKPQKFWAWKTYXBHZA | 0.98 | 2307251 | 2022-08-26 22:16:51 UTC
0F3JD4RWDVB4HXBPJ4DR39B5CE | 0.57 | 2307251 | 2022-08-26 22:17:00 UTC
0F3JD4VKNR0FRVVZKNGXHNGRF6 | -2.65 | 2307251 | 2022-08-26 22:17:09 UTC
0F3JD4Y9YSZWM4MWVSBJ3WJ6QW | 1.72 | 2307251 | 2022-08-26 22:17:17 UTC
0F3JD51ASRYP8BKDHTD57GS6DF | 0.80 | 2307251 | 2022-08-26 22:17:27 UTC
0F3JD543ABSQH81GGEA5XDE1JG | -4.11 | 2307251 | 2022-08-26 22:17:36 UTC
0F3JD56RVG8DE7BJJMMPQ8F8QK | -0.97 | 2307251 | 2022-08-26 22:17:45 UTC
0F3JD59FMP55M8BK3GJ0E01JY4 | -0.08 | 2307251 | 2022-08-26 22:17:54 UTC
0F3JD5C6J0YD4KHQ3MWQ5RKET6 | -1.04 | 2307251 | 2022-08-26 22:18:03 UTC
0F3JD5EXMN2BXS56AM67DBFM67 | -2.10 | 2307251 | 2022-08-26 22:18:12 UTC
0F3JD5HM71DNFCJ6QSH9NM33M1 | -1.00 | 2307251 | 2022-08-26 22:18:21 UTC
0F3JD5MAXSYQ8FSGZ2JH3A0SRK | -0.75 | 2307251 | 2022-08-26 22:18:30 UTC
0F3JD5QC682VHN9QJEZWSFQ4V0 | 1.11 | 2307251 | 2022-08-26 22:18:40 UTC
0F3JD5T3ARPRS75KDC7PYR062Y | 2.58 | 2307251 | 2022-08-26 22:18:49 UTC
0F3JD5WT1JXMD0KJ3EEHHMHWSF | 1.55 | 2307251 | 2022-08-26 22:18:57 UTC
0F3JD5ZGZYFY92G3RMV2EAE3TJ | 1.65 | 2307251 | 2022-08-26 22:19:06 UTC
0F3JD627WVA2531FAB2KY7H2FY | -5.54 | 2307251 | 2022-08-26 22:19:15 UTC
0F3JD64Y9CA5RRZPR0X9JVHZD4 | 0.50 | 2307251 | 2022-08-26 22:19:24 UTC
0F3JD67NZ8CWAMVEJQ9N3PWKSX | -2.88 | 2307251 | 2022-08-26 22:19:33 UTC
0F3JD6AC78EW3S2140H7ZB0BX8 | 1.15 | 2307251 | 2022-08-26 22:19:42 UTC
0F3JD6D3BNTNEFERMQXG7RFZ3X | -4.97 | 2307251 | 2022-08-26 22:19:51 UTC
0F3JD6FT8JNSHKE96G9G24TZGR | -2.68 | 2307251 | 2022-08-26 22:20:00 UTC
0F3JD6JTHK176NWNZGN4W1PHQ4 | -3.37 | 2307251 | 2022-08-26 22:20:10 UTC
0F3JD6NHFVMJMNMCY9J09NN23A | 0.09 | 2307251 | 2022-08-26 22:20:18 UTC
0F3JD6R9E8H02QCMY967AAFB6P | -1.22 | 2307251 | 2022-08-26 22:20:27 UTC
0F3JD6V11ARYR2810FMXMFSDGM | 1.30 | 2307251 | 2022-08-26 22:20:36 UTC
0F3JD6XPMHM3W1X7183TT6PAXK | -2.43 | 2307251 | 2022-08-26 22:20:45 UTC
0F3JD70DDYS39EZQY9CAAH6E8R | 4.59 | 2307251 | 2022-08-26 22:20:54 UTC
0F3JD7351SGAQZDQ1H5DXKVQHA | -3.45 | 2307251 | 2022-08-26 22:21:03 UTC
0F3JD75ZKESE54F1HAMFFQEWEJ | 0.96 | 2307251 | 2022-08-26 22:21:12 UTC
0F3JD78K4P3XBV5TNQTSBVS73K | -3.67 | 2307251 | 2022-08-26 22:21:21 UTC
0F3JD7BKNA4WG4KBBP9RX0JKSX | -3.74 | 2307251 | 2022-08-26 22:21:31 UTC
0F3JD7EEBQPP15KNH8RERD15A8 | -2.87 | 2307251 | 2022-08-26 22:21:40 UTC
0F3JD7H0YXY4TDY6T6FCJ2NH2Z | 1.31 | 2307251 | 2022-08-26 22:21:49 UTC
0F3JD7KQQ4Q0QRDH1KFC00Y2H5 | -4.30 | 2307251 | 2022-08-26 22:21:57 UTC
0F3JD7PETV2ADHVN03D2J4TZH0 | -0.80 | 2307251 | 2022-08-26 22:22:06 UTC
0F3JD7S72HHAG9BHCPHP2YYCBN | 2.89 | 2307251 | 2022-08-26 22:22:15 UTC
0F3JD7VXEG90ABGEE1TZHXD3QG | 0.00 | 2307251 | 2022-08-26 22:22:24 UTC
0F3JD7YMWJ9DZWSZPTQY9579BR | -4.28 | 2307251 | 2022-08-26 22:22:33 UTC
0F3JD81CPCENBYJ71XRNW8S6JT | -3.76 | 2307251 | 2022-08-26 22:22:42 UTC
0F3JD843Y68C3FGEAXGQZD7TDG | 24.45 | 2307251 | 2022-08-26 22:22:51 UTC
0F3JD86VS5EQF7WV35CPAXEAWN | 95.34 | 2307251 | 2022-08-26 22:23:00 UTC
0F3JD89K3RAP7FYDF1S87YY6SX | 168.02 | 2307251 | 2022-08-26 22:23:09 UTC
0F3JD8CM2VM5C5J33ADBNC2PWZ | 200.04 | 2307251 | 2022-08-26 22:23:19 UTC
0F3JD8FB1XZ4AVT6R13XCHEMQG | 222.02 | 2307251 | 2022-08-26 22:23:28 UTC
0F3JD8J64864VW765P0A9GPANR | 231.80 | 2307251 | 2022-08-26 22:23:37 UTC
0F3JD8MTKQ632ADA44B97BGD1R | 229.57 | 2307251 | 2022-08-26 22:23:46 UTC
0F3JD8QH745HTTY4V06SC5M5SG | 223.44 | 2307251 | 2022-08-26 22:23:55 UTC
0F3JD8T9A2179Y5W4YFPFEWK2V | 219.82 | 2307251 | 2022-08-26 22:24:04 UTC
0F3JD8X0E34PAF8FW0RDJKGNV8 | 223.07 | 2307251 | 2022-08-26 22:24:13 UTC
0F3JD8ZQFCQFNRFCN83DS4QGGV | 221.69 | 2307251 | 2022-08-26 22:24:22 UTC
0F3JD92F2210WDAHNAK9QSBD8Q | 217.41 | 2307251 | 2022-08-26 22:24:31 UTC
0F3JD95BB4YXPVE17W0TX864T3 | 214.04 | 2307251 | 2022-08-26 22:24:40 UTC
0F3JD97XWAPFF1KEVRGAPEZ12G | 210.45 | 2307251 | 2022-08-26 22:24:48 UTC
0F3JD9ANBT2DG3GKBTHGT2XXX8 | 206.49 | 2307251 | 2022-08-26 22:24:57 UTC
0F3JD9DCPJS6XD5BRE4QFSAV7Z | 203.49 | 2307251 | 2022-08-26 22:25:06 UTC
0F3JD9G445J84ZS1Y4W69JBVJM | 197.94 | 2307251 | 2022-08-26 22:25:15 UTC
0F3JD9JWEYBCVKE4ST4EK2YR7Q | 197.11 | 2307251 | 2022-08-26 22:25:24 UTC
0F3JD9NXEMVC8Y5JR2T6K8W0RC | 193.36 | 2307251 | 2022-08-26 22:25:34 UTC
0F3JD9RM9GRYBM9JE321GPJ2W1 | 189.03 | 2307251 | 2022-08-26 22:25:43 UTC
0F3JD9VBDRNV1CWKD0ZRFWF75F | 182.61 | 2307251 | 2022-08-26 22:25:52 UTC
0F3JD9Y38C7WMDMSEJ7HAH632B | 174.21 | 2307251 | 2022-08-26 22:26:01 UTC
0F3JDA0VYXXNGHR83WTDF1F3XW | 166.72 | 2307251 | 2022-08-26 22:26:10 UTC
0F3JDA3HZ5VNEXC1SSK0TBN088 | 164.29 | 2307251 | 2022-08-26 22:26:19 UTC
0F3JDA691KFKNG7340KT6T668J | 152.48 | 2307251 | 2022-08-26 22:26:28 UTC
0F3JDA9485N2RG0718KT4AGS2P | 149.06 | 2307251 | 2022-08-26 22:26:37 UTC
0F3JDABRGN5WMYXR3Y9MDC8F19 | 141.68 | 2307251 | 2022-08-26 22:26:46 UTC
0F3JDAEEXPH7RQZSE74C4WJWJ0 | 135.39 | 2307251 | 2022-08-26 22:26:55 UTC
0F3JDAH72GDEJTCYFEKY65D60W | 138.62 | 2307251 | 2022-08-26 22:27:04 UTC
0F3JDAKYBTNRV49B9BQJED6C37 | 135.79 | 2307251 | 2022-08-26 22:27:13 UTC
0F3JDAPNGNQCACRYQYFFGJ6K5Q | 133.59 | 2307251 | 2022-08-26 22:27:22 UTC
0F3JDASD7TZCF1KS4Z4QEZC2PW | 132.15 | 2307251 | 2022-08-26 22:27:31 UTC
0F3JDAWB0T8RW424VYP8HR92ED | 134.28 | 2307251 | 2022-08-26 22:27:40 UTC
0F3JDAYW6WF0P8KE2ZHAMY5RZD | 137.22 | 2307251 | 2022-08-26 22:27:48 UTC
0F3JDB1WZDNQS3P0M4RT6MWNPF | 132.42 | 2307251 | 2022-08-26 22:27:58 UTC
0F3JDB4M4J1D1Y0X9S36P1JQ1G | 131.32 | 2307251 | 2022-08-26 22:28:07 UTC
0F3JDB7B5PTMVWSPQSPFYVRANH | 129.01 | 2307251 | 2022-08-26 22:28:16 UTC
0F3JDBA2JAC4TBGB4XT6GKA2Y9 | 128.03 | 2307251 | 2022-08-26 22:28:25 UTC
0F3JDBCT14NAEV2H5W8R56PWFZ | 119.28 | 2307251 | 2022-08-26 22:28:34 UTC
0F3JDBFJ2X5YMTVXA309PT367Q | 125.48 | 2307251 | 2022-08-26 22:28:43 UTC
0F3JDBJ97GS7738VZRAAMHTWNH | 124.60 | 2307251 | 2022-08-26 22:28:52 UTC
0F3JDBN0GZPSHQYR3JSXPKRTK4 | 118.45 | 2307251 | 2022-08-26 22:29:01 UTC
0F3JDBQQTHQXVTW73828QDV4M6 | 115.15 | 2307251 | 2022-08-26 22:29:10 UTC
0F3JDBTFJCST52N25XYMQQCDG6 | 117.60 | 2307251 | 2022-08-26 22:29:19 UTC
0F3JDBX6FBJC2XZ3PWFFEWHC4R | 115.44 | 2307251 | 2022-08-26 22:29:28 UTC
0F3JDC0284FMWTDTQT5YFBR9NT | 115.14 | 2307251 | 2022-08-26 22:29:37 UTC
0F3JDC2NHKK7QKZ8PFHVGJJZBM | 109.00 | 2307251 | 2022-08-26 22:29:46 UTC
0F3JDC5CYAK3A06CFPXKAM00XF | 109.93 | 2307251 | 2022-08-26 22:29:55 UTC
0F3JDC851MKAY8H7CMBSVXYC1D | 106.68 | 2307251 | 2022-08-26 22:30:04 UTC
0F3JDCAVKCA75BSR0PXPJRP7CE | 105.50 | 2307251 | 2022-08-26 22:30:13 UTC
0F3JDCDXJ286BAD2PZP2XBEQ9Z | 108.20 | 2307251 | 2022-08-26 22:30:23 UTC
0F3JDCGMHNTGN2GJECNY75EP6W | 103.88 | 2307251 | 2022-08-26 22:30:32 UTC
0F3JDCKD6RBVW9QE3ENNM9J8W7 | 98.70 | 2307251 | 2022-08-26 22:30:41 UTC
0F3JDCP339JC2EZRKXZHZQWHYD | 100.17 | 2307251 | 2022-08-26 22:30:49 UTC
0F3JDCRTGEQRMM6F5J82W8FMHD | 92.41 | 2307251 | 2022-08-26 22:30:58 UTC
0F3JDCVJ85SXJ8QE906ZHGFAAR | 96.27 | 2307251 | 2022-08-26 22:31:07 UTC
0F3JDCY9997VQ6C535QCGA7GX1 | 92.35 | 2307251 | 2022-08-26 22:31:16 UTC
0F3JDD10FGV2EX9C3K5F9C886D | 87.10 | 2307251 | 2022-08-26 22:31:25 UTC
0F3JDD3R66X2FBHPQ2843Q1D83 | 90.18 | 2307251 | 2022-08-26 22:31:34 UTC
0F3JDD6FRF641A80T7DBVTV827 | 86.45 | 2307251 | 2022-08-26 22:31:43 UTC
0F3JDD96WTEBD79VFRT15Z66QE | 86.89 | 2307251 | 2022-08-26 22:31:52 UTC
0F3JDDBYD6HEXXBT1PJ4AG8TXC | 87.78 | 2307251 | 2022-08-26 22:32:01 UTC
0F3JDDENZE6MSNW46FYY011BPZ | 85.44 | 2307251 | 2022-08-26 22:32:10 UTC
0F3JDDHDREG6RRTBZX3VVQSXYZ | 81.69 | 2307251 | 2022-08-26 22:32:19 UTC
0F3JDDM518YVC8K1DGMDYKBWSX | 82.71 | 2307251 | 2022-08-26 22:32:28 UTC
0F3JDDQ04ZPHVZK12JVWJQPXKB | 79.25 | 2307251 | 2022-08-26 22:32:37 UTC
0F3JDDSWZ4JP5FQ1PR3ZAG05R4 | 80.91 | 2307251 | 2022-08-26 22:32:47 UTC
0F3JDDWM2R9P3JF332G2B8PDHH | 74.89 | 2307251 | 2022-08-26 22:32:56 UTC
0F3JDDZC1KAJ6Z7T12KME38W2E | 75.53 | 2307251 | 2022-08-26 22:33:05 UTC
0F3JDE22GKJSN6PAD2S4QN675B | 75.13 | 2307251 | 2022-08-26 22:33:14 UTC
0F3JDE4SRC2K2RZKJH727899C1 | 79.88 | 2307251 | 2022-08-26 22:33:22 UTC
0F3JDE7HBT9W4YC12QMK3K3J39 | 72.56 | 2307251 | 2022-08-26 22:33:31 UTC
0F3JDEAAFCPG3KE32A5NS1AE2D | 73.44 | 2307251 | 2022-08-26 22:33:41 UTC
0F3JDECZTMG6KXKKWK2WTRV1QB | 71.19 | 2307251 | 2022-08-26 22:33:49 UTC
0F3JDEFPXH16RVK8WJW5SW5AJF | 77.70 | 2307251 | 2022-08-26 22:33:58 UTC
0F3JDEJE80RYJVV2MH0JHVG928 | 65.79 | 2307251 | 2022-08-26 22:34:07 UTC
0F3JDEN5ZHVYBF01J7GCK2K86Q | 69.73 | 2307251 | 2022-08-26 22:34:16 UTC
0F3JDEQXE4NV2PGBA7EECZT6DY | 63.14 | 2307251 | 2022-08-26 22:34:25 UTC
0F3JDETMC58K7BEH25DKSMBG1Q | 65.55 | 2307251 | 2022-08-26 22:34:34 UTC
0F3JDEXN7KZ3G3HH4XZSVX5DKH | 64.80 | 2307251 | 2022-08-26 22:34:44 UTC
0F3JDF0BZG5GVXT804H0XM8981 | 61.33 | 2307251 | 2022-08-26 22:34:53 UTC
0F3JDF33YEJPM93CWKN43BB5TE | 59.74 | 2307251 | 2022-08-26 22:35:02 UTC
0F3JDF5WDKWK2YC0DH8SP2KBM6 | 58.32 | 2307251 | 2022-08-26 22:35:11 UTC
0F3JDF8HRPK20YHYB370X80RNZ | 60.29 | 2307251 | 2022-08-26 22:35:20 UTC
0F3JDFB9G6EM5MYZXJV7B2H8S4 | 54.61 | 2307251 | 2022-08-26 22:35:29 UTC
0F3JDFE5Z7HCKSZ030EQS39HPE | 56.76 | 2307251 | 2022-08-26 22:35:38 UTC
0F3JDFGRMP6232MVCKKM5SC7FQ | 56.86 | 2307251 | 2022-08-26 22:35:47 UTC
0F3JDFKF68HDJQPCXAKM4WMMVT | 56.34 | 2307251 | 2022-08-26 22:35:55 UTC
0F3JDFP6636B1DQ2EH6TTS1XE1 | 50.94 | 2307251 | 2022-08-26 22:36:04 UTC
0F3JDFRY2HE7H1ZT5KBE34W5HF | 55.36 | 2307251 | 2022-08-26 22:36:13 UTC
0F3JDFVMS6HDF7S2YX321K80P2 | 51.47 | 2307251 | 2022-08-26 22:36:22 UTC
0F3JDFYNDPZ95S0BBZFFV63Z3R | 52.28 | 2307251 | 2022-08-26 22:36:32 UTC
0F3JDG1D813Z0D4PQSPVHP1996 | 48.17 | 2307251 | 2022-08-26 22:36:41 UTC
0F3JDG447HEFA8HB5CAJFA0WQN | 46.53 | 2307251 | 2022-08-26 22:36:50 UTC
0F3JDG6VB1Y6TQY1HM8W4QJ6W9 | 45.08 | 2307251 | 2022-08-26 22:36:59 UTC
0F3JDG9JABYC2ZKEJ0SX6T83EN | 46.17 | 2307251 | 2022-08-26 22:37:08 UTC
0F3JDGCA0RREHBM0M1G5WP0BTH | 46.27 | 2307251 | 2022-08-26 22:37:17 UTC
0F3JDGF0ZFJ9E83AXKS5TGSE9S | 43.99 | 2307251 | 2022-08-26 22:37:26 UTC
0F3JDGHRQ22V1K9SJ3TMYF0BJT | 40.06 | 2307251 | 2022-08-26 22:37:35 UTC
0F3JDGMFFN04FG28HJFY2Y669C | 36.32 | 2307251 | 2022-08-26 22:37:44 UTC
0F3JDGQ749GNEX7X9TNP6FE95K | 41.60 | 2307251 | 2022-08-26 22:37:53 UTC
0F3JDGT9KX9WQW1VDVZ3JMTPXS | 38.88 | 2307251 | 2022-08-26 22:38:03 UTC
0F3JDGWNE2GGM7AVCD9PYFZP0P | 41.70 | 2307251 | 2022-08-26 22:38:10 UTC
0F3JDGZD54XGBRCSVRTJNG42J2 | 41.96 | 2307251 | 2022-08-26 22:38:19 UTC
0F3JDH2DJBYQDNQ58B9GV9E09A | 36.98 | 2307251 | 2022-08-26 22:38:29 UTC
0F3JDH5C0HZDHSYM7QTBHJ7Q7B | 37.54 | 2307251 | 2022-08-26 22:38:39 UTC
0F3JDH7WC84WQZB6ZQXFMPRFYP | 37.85 | 2307251 | 2022-08-26 22:38:47 UTC
0F3JDHAPCMH353DB4PXF6H6H0E | 36.93 | 2307251 | 2022-08-26 22:38:56 UTC
0F3JDHDARB0XG30RP9P8WCJ1NV | 35.00 | 2307251 | 2022-08-26 22:39:05 UTC
0F3JDHG274SGETN3FBR0DZ0VB5 | 31.60 | 2307251 | 2022-08-26 22:39:14 UTC
0F3JDHJS90TJ0VXFRBK5XNXC8E | 34.08 | 2307251 | 2022-08-26 22:39:23 UTC
0F3JDHNGP8B2V6R0TKBWR7VYH0 | 31.39 | 2307251 | 2022-08-26 22:39:32 UTC
0F3JDHR80DV26127NNST0AF7SB | 34.03 | 2307251 | 2022-08-26 22:39:41 UTC
0F3JDHTZ9D1F973V9MBHRZG831 | 33.28 | 2307251 | 2022-08-26 22:39:50 UTC
0F3JDHXP3Q5EZVV0XSX416QXAX | 29.12 | 2307251 | 2022-08-26 22:39:59 UTC
0F3JDJ0DBQG2B7426K0N9FN63P | 32.23 | 2307251 | 2022-08-26 22:40:08 UTC
0F3JDJ36F7GF5HTPTZZX09FGPW | 26.89 | 2307251 | 2022-08-26 22:40:17 UTC
0F3JDJ669J30FE0ETMTH4XNA6Q | 28.00 | 2307251 | 2022-08-26 22:40:26 UTC
0F3JDJ9AH0AHDNTY4219SMAJXZ | 28.22 | 2307251 | 2022-08-26 22:40:37 UTC
0F3JDJBN03AZGY7D9TWRF0HS1T | 27.85 | 2307251 | 2022-08-26 22:40:44 UTC
0F3JDJEBFCD95VE4SKA8S8RRMW | 27.92 | 2307251 | 2022-08-26 22:40:53 UTC
0F3JDJH35C4R2GJEZE87MTR1A0 | 29.83 | 2307251 | 2022-08-26 22:41:02 UTC
0F3JDJKSW4AWP3KR3EJZ4JD96Z | 26.94 | 2307251 | 2022-08-26 22:41:11 UTC
0F3JDJPJ8JHRDCNZDM9WBGR09M | 26.24 | 2307251 | 2022-08-26 22:41:20 UTC
0F3JDJS93EQCNYS3D9JX8JD292 | 27.19 | 2307251 | 2022-08-26 22:41:29 UTC
0F3JDJW5B9MEXNMJKZEMGX5BBZ | 23.73 | 2307251 | 2022-08-26 22:41:38 UTC
0F3JDJYQ998FP70BV3NWMNP0BA | 24.61 | 2307251 | 2022-08-26 22:41:47 UTC
0F3JDK1E9RESD7YHQCMK8HYA3K | 26.72 | 2307251 | 2022-08-26 22:41:56 UTC
0F3JDK464VDYKG2TK8Z56S86BH | 28.67 | 2307251 | 2022-08-26 22:42:05 UTC
0F3JDK6WYCPCSTFNFPH5583FZF | 27.12 | 2307251 | 2022-08-26 22:42:14 UTC
0F3JDK9Y11TPQVHAQKCZM3GJA8 | 23.41 | 2307251 | 2022-08-26 22:42:24 UTC
0F3JDKCN1H6B6HA9YGKWYT1XBM | 26.06 | 2307251 | 2022-08-26 22:42:32 UTC
0F3JDKFCMYH36DJH43GFMSH52X | 17.73 | 2307251 | 2022-08-26 22:42:41 UTC
0F3JDKJ44N761XAXCVF19RHR04 | 25.21 | 2307251 | 2022-08-26 22:42:50 UTC
0F3JDKMV99G96WHK6KBFA84GH9 | 22.73 | 2307251 | 2022-08-26 22:42:59 UTC
0F3JDKQJ75C43XKGWAHVW3ZB2J | 18.72 | 2307251 | 2022-08-26 22:43:08 UTC
0F3JDKT9C35TTFHF0G1M80CC2A | 23.06 | 2307251 | 2022-08-26 22:43:17 UTC
0F3JDKX10F39K1SG3ZYPNARVCB | 21.21 | 2307251 | 2022-08-26 22:43:26 UTC
0F3JDKZR0D20241132VMQ0PPZ8 | 21.20 | 2307251 | 2022-08-26 22:43:35 UTC
0F3JDM2FPF1C3RPMT6DFA66XWD | 22.98 | 2307251 | 2022-08-26 22:43:44 UTC
0F3JDM56YTPDR2NJXKEBKH9Y50 | 20.78 | 2307251 | 2022-08-26 22:43:53 UTC
0F3JDM7Y1RYCD5GFXR39ECTN9A | 17.61 | 2307251 | 2022-08-26 22:44:02 UTC
0F3JDMANC3GW8YP9K6ZQS3WJDN | 18.14 | 2307251 | 2022-08-26 22:44:11 UTC
0F3JDMDP8DJ0RQJT80D92SK2NR | 20.02 | 2307251 | 2022-08-26 22:44:21 UTC
0F3JDMGDCRRYAJVXQSQB0MK8NN | 19.11 | 2307251 | 2022-08-26 22:44:30 UTC
0F3JDMKD8GAQX8DYP35KT11M4M | 20.81 | 2307251 | 2022-08-26 22:44:39 UTC
0F3JDMNW0ANQ0572QPT6X5MC99 | 19.82 | 2307251 | 2022-08-26 22:44:48 UTC
0F3JDMRKXYTPJT8QS3PATBMBA2 | 18.13 | 2307251 | 2022-08-26 22:44:57 UTC
0F3JDMVAXBHZ9RAGWT7NQVFHNX | 11.06 | 2307251 | 2022-08-26 22:45:05 UTC
0F3JDMY1XAWGSQBFVRFGF2DVZ5 | 17.80 | 2307251 | 2022-08-26 22:45:14 UTC
0F3JDN0SKEAV2J42XZ4KWKC3J1 | 15.47 | 2307251 | 2022-08-26 22:45:23 UTC
0F3JDN3GDDGDSZNMK88XY5P2T8 | 10.82 | 2307251 | 2022-08-26 22:45:32 UTC
0F3JDN67KS4YES9EKRSSB2DFE3 | 16.32 | 2307251 | 2022-08-26 22:45:41 UTC
0F3JDN8Z6V3S0T8TMK1DY4NNXA | 12.30 | 2307251 | 2022-08-26 22:45:50 UTC
0F3JDNBNZG32SK66QRFQ5JB80Z | 14.69 | 2307251 | 2022-08-26 22:45:59 UTC
0F3JDNEDKWCNZG692VE1HNCPAT | 13.57 | 2307251 | 2022-08-26 22:46:08 UTC
0F3JDNHEEH5XHMT8GXP1QEQ2YD | 14.06 | 2307251 | 2022-08-26 22:46:18 UTC
0F3JDNM6BCQGMJ9EYSJ1KJDR4T | 12.91 | 2307251 | 2022-08-26 22:46:27 UTC
0F3JDNPWTA497PHF2K6W745NHP | 13.59 | 2307251 | 2022-08-26 22:46:36 UTC
0F3JDNSMQC5XN0QJVMC21N849T | 17.44 | 2307251 | 2022-08-26 22:46:45 UTC
0F3JDNWBVHE4EETH0WNBH7PDYN | 14.44 | 2307251 | 2022-08-26 22:46:54 UTC
0F3JDNZ2GDRK1QCFV0G83SZP51 | 13.43 | 2307251 | 2022-08-26 22:47:03 UTC
0F3JDP1SNPPYPMP4QFPEMC6NHJ | 10.44 | 2307251 | 2022-08-26 22:47:11 UTC
0F3JDP4H63JJS542CDT80AXRXD | 14.78 | 2307251 | 2022-08-26 22:47:20 UTC
0F3JDP78NZR8KJZSWDQHBPKJNG | 7.59 | 2307251 | 2022-08-26 22:47:29 UTC
0F3JDPA7TP71TFFAZ97JJZYMCZ | 12.11 | 2307251 | 2022-08-26 22:47:39 UTC
0F3JDPCQ8805Z1QG2FYQ25YC2R | 13.05 | 2307251 | 2022-08-26 22:47:47 UTC
0F3JDPFE76DYZQE2GGKBG8WZ6W | 15.97 | 2307251 | 2022-08-26 22:47:56 UTC
0F3JDPJFDRDSM3B6SFVRNJKZEJ | 16.08 | 2307251 | 2022-08-26 22:48:06 UTC
0F3JDPN615JJMNMH2PY7ZTKJPB | 16.59 | 2307251 | 2022-08-26 22:48:15 UTC
0F3JDPQXD5GPPRFZCS7YZVTV56 | 6.67 | 2307251 | 2022-08-26 22:48:24 UTC
0F3JDPTN8M6MEY85ES3SR15R8B | 14.29 | 2307251 | 2022-08-26 22:48:33 UTC
0F3JDPXC3MV2PMRK9PEEXACKA5 | 11.27 | 2307251 | 2022-08-26 22:48:42 UTC
0F3JDQ044XKDZZG3N6DB5F4JRF | 9.37 | 2307251 | 2022-08-26 22:48:51 UTC
0F3JDQ2TVX5E3VYPC2RSFKZVRG | 13.60 | 2307251 | 2022-08-26 22:49:00 UTC
0F3JDQ5J0J3E2WSPR03M7J0PGB | 10.74 | 2307251 | 2022-08-26 22:49:09 UTC
0F3JDQ892YX069G4M4AATPV5FD | 11.33 | 2307251 | 2022-08-26 22:49:18 UTC
0F3JDQB0HF29VSH1SW6NAJYBX8 | 6.06 | 2307251 | 2022-08-26 22:49:27 UTC
0F3JDQDQK205BGPRT3FSSZ9FZM | 10.49 | 2307251 | 2022-08-26 22:49:35 UTC
0F3JDQGEZ8PP0GG790HGEHHYTN | 11.12 | 2307251 | 2022-08-26 22:49:44 UTC
0F3JDQK6E4047XH4WPZQZKPS4Q | 10.32 | 2307251 | 2022-08-26 22:49:53 UTC
0F3JDQP897ER17NKHV1GWXV1K5 | 8.76 | 2307251 | 2022-08-26 22:50:03 UTC
0F3JDQRYK520ACSQEPMMTNYS7F | 11.02 | 2307251 | 2022-08-26 22:50:12 UTC
0F3JDQVNP8Q77YPYFZ8GKFYEFD | 11.14 | 2307251 | 2022-08-26 22:50:21 UTC
0F3JDQYCW78RPDCABA782KFFPY | 9.29 | 2307251 | 2022-08-26 22:50:30 UTC
0F3JDR1AG7AR8A45R3KAVKFFAN | 6.96 | 2307251 | 2022-08-26 22:50:40 UTC
0F3JDR3V2XXCC04Y2M9QRNV0Y3 | 8.97 | 2307251 | 2022-08-26 22:50:48 UTC
0F3JDR6J8X5450TXK2BK626Y02 | 7.60 | 2307251 | 2022-08-26 22:50:57 UTC
0F3JDR99HRAKPR88E4T3WXHEYN | 8.55 | 2307251 | 2022-08-26 22:51:06 UTC
0F3JDRC0KQK9HJBF9T6JSRBRG9 | 10.54 | 2307251 | 2022-08-26 22:51:15 UTC
0F3JDREQJ68PWXM6WKB1N79JWC | 10.59 | 2307251 | 2022-08-26 22:51:24 UTC
0F3JDRHEJTJF34KCABX6PF0SA9 | 10.83 | 2307251 | 2022-08-26 22:51:33 UTC
0F3JDRMFX1JGDSTSZTVV5KST1Y | 6.53 | 2307251 | 2022-08-26 22:51:42 UTC
0F3JDRQ67N2H5VQNE3W4KPQ12V | 7.83 | 2307251 | 2022-08-26 22:51:51 UTC
0F3JDRSXTNBATW1YQ7B5ZVSFV2 | 11.28 | 2307251 | 2022-08-26 22:52:00 UTC
0F3JDRWME0YMNSWT8PJZMNF4H0 | 14.53 | 2307251 | 2022-08-26 22:52:09 UTC
0F3JDRZBZ0TXGAFPKR0DSBWY0B | 6.27 | 2307251 | 2022-08-26 22:52:18 UTC
0F3JDS238XDBTDFZJ0QGENRAP4 | 6.36 | 2307251 | 2022-08-26 22:52:27 UTC
0F3JDS4TYFBHWN66MP0P9MS5FT | 6.11 | 2307251 | 2022-08-26 22:52:36 UTC
0F3JDS7HMTMC3WEF9QN27C5DWT | 13.38 | 2307251 | 2022-08-26 22:52:45 UTC
0F3JDSA92C4KHTSBMG461E86WC | 5.81 | 2307251 | 2022-08-26 22:52:54 UTC
0F3JDSCZE0ZPJGQ3FJQS7KWCQB | 7.24 | 2307251 | 2022-08-26 22:53:03 UTC
0F3JDSFP8FARQTTXVAS4VTFGS0 | 7.22 | 2307251 | 2022-08-26 22:53:12 UTC
0F3JDSJPZ1Q5G4VZS9XTNBNR5B | 6.74 | 2307251 | 2022-08-26 22:53:21 UTC
0F3JDSNFCNQT8VP5MW710WQFQG | 6.52 | 2307251 | 2022-08-26 22:53:31 UTC
0F3JDSR9X6T82B281BQYR7PHGA | 5.87 | 2307251 | 2022-08-26 22:53:40 UTC
0F3JDSTWGK1MK5E60GTEZ15BTG | 4.47 | 2307251 | 2022-08-26 22:53:48 UTC
0F3JDSXKHS3VR6Y7N2JAPFW10Y | 5.26 | 2307251 | 2022-08-26 22:53:57 UTC
0F3JDT0AFPK4D9TYA1P695EGEF | 8.03 | 2307251 | 2022-08-26 22:54:06 UTC
0F3JDT31GRCRYSM28ZQCG1NFRK | 5.69 | 2307251 | 2022-08-26 22:54:15 UTC
0F3JDT5S0QBGS3WBNFVQV8F3KX | 4.43 | 2307251 | 2022-08-26 22:54:24 UTC
0F3JDT8FVPF3KR1P4QKVZJRC6Z | 9.29 | 2307251 | 2022-08-26 22:54:33 UTC
0F3JDTB71TECA40K4CV9ZHE8XH | 5.66 | 2307251 | 2022-08-26 22:54:42 UTC
0F3JDTE7NYPRWD027H5FMJA8YC | 5.95 | 2307251 | 2022-08-26 22:54:52 UTC
0F3JDTGYSVWC6V6AC6CSEN2AAK | 7.77 | 2307251 | 2022-08-26 22:55:01 UTC
0F3JDTKPACG75B4ENAMD0TGFSK | 10.15 | 2307251 | 2022-08-26 22:55:10 UTC
0F3JDTPDJK1NKX16E7A0KTED7T | 8.48 | 2307251 | 2022-08-26 22:55:18 UTC
0F3JDTS46J5E77HS5BXW6D4786 | 9.01 | 2307251 | 2022-08-26 22:55:27 UTC
0F3JDTVXVAEHGCHV17FYXRHMKH | 1.19 | 2307251 | 2022-08-26 22:55:37 UTC
0F3JDTYJ7TAR2GR9R0SHR5476M | 1.02 | 2307251 | 2022-08-26 22:55:45 UTC
0F3JDV19CGJH8D7NS6AJA5PBTW | 8.91 | 2307251 | 2022-08-26 22:55:54 UTC
0F3JDV41AZAHGFQ9SX1TT2S20Q | 5.49 | 2307251 | 2022-08-26 22:56:03 UTC
0F3JDV6QKCTGXBBF9HBFXPE8JW | 3.56 | 2307251 | 2022-08-26 22:56:12 UTC
0F3JDV9F1BYSVWR601MZ8VKQQ6 | 0.28 | 2307251 | 2022-08-26 22:56:21 UTC
0F3JDVCF8JSXRHSG7V14NQKHCP | 6.64 | 2307251 | 2022-08-26 22:56:31 UTC
0F3JDVF9WMCJGJK7F9WKGNGWWM | 3.41 | 2307251 | 2022-08-26 22:56:40 UTC
0F3JDVHXS1DJ56EXE3WSBNSFP9 | 1.80 | 2307251 | 2022-08-26 22:56:49 UTC
0F3JDVMMSJH97P1G753Q8MHSDN | 3.28 | 2307251 | 2022-08-26 22:56:58 UTC
0F3JDVQBQNZ54MJJRKEVJH4MBF | 4.73 | 2307251 | 2022-08-26 22:57:06 UTC
0F3JDVT2KAE1RF58VM5CN1XG9V | 5.86 | 2307251 | 2022-08-26 22:57:15 UTC
0F3JDVWSSJV30Z1NYQ0J5ZBM18 | 7.77 | 2307251 | 2022-08-26 22:57:24 UTC
0F3JDVZH4YAN30B99ADAFNWP99 | 10.31 | 2307251 | 2022-08-26 22:57:33 UTC
0F3JDW2806HGWWVQGECM6RJ1WT | -1.76 | 2307251 | 2022-08-26 22:57:42 UTC
0F3JDW4Z8AG534CFGDMZZ87GGK | 2.26 | 2307251 | 2022-08-26 22:57:51 UTC
0F3JDW805KDG7DBWJFG3GYFYFJ | 3.91 | 2307251 | 2022-08-26 22:58:01 UTC
0F3JDWAPXM5KEG4F772C9PDTMB | 3.99 | 2307251 | 2022-08-26 22:58:10 UTC
0F3JDWDE880YP69GM6HKVGVD7T | 7.64 | 2307251 | 2022-08-26 22:58:19 UTC
0F3JDWG5GFRDN1HFSTNNT320FZ | 6.40 | 2307251 | 2022-08-26 22:58:28 UTC
0F3JDWJZET3MVAK5XYC2J280Q9 | 6.60 | 2307251 | 2022-08-26 22:58:37 UTC
0F3JDWNKP6EGZYGBBD2BN3CS7V | 2.60 | 2307251 | 2022-08-26 22:58:46 UTC
0F3JDWRAHDNXHB0HKQT060E7RC | 1.02 | 2307251 | 2022-08-26 22:58:54 UTC
0F3JDWV1QDHVGVWZNMBDHYSZP5 | 6.35 | 2307251 | 2022-08-26 22:59:03 UTC
0F3JDWXRRBQR9982QV2HNBXP7P | 6.18 | 2307251 | 2022-08-26 22:59:12 UTC
0F3JDX0J0GVDVNRHJNPF4W44E8 | 4.40 | 2307251 | 2022-08-26 22:59:21 UTC
0F3JDX3GQX6TY2PQQNWQJRNP60 | 4.58 | 2307251 | 2022-08-26 22:59:31 UTC
0F3JDX69R1W77NXMMECXEY316V | 0.68 | 2307251 | 2022-08-26 22:59:40 UTC
0F3JDX8YZ9SEZ591KXC256K7CD | -1.00 | 2307251 | 2022-08-26 22:59:49 UTC
0F3JDXBNQ7BK6887DC342SS8AX | 3.72 | 2307251 | 2022-08-26 22:59:58 UTC
0F3JDXECZH4PA8X1V34WGD2VB3 | 0.92 | 2307251 | 2022-08-26 23:00:07 UTC
0F3JDXH45CJF8CCP6Y0HHRDFN8 | 2.88 | 2307251 | 2022-08-26 23:00:16 UTC
0F3JDXKVHP2GXVNETPNPEGMPQW | 2.98 | 2307251 | 2022-08-26 23:00:25 UTC
0F3JDXPJD648WRYWHBFDVK4AGN | 0.23 | 2307251 | 2022-08-26 23:00:34 UTC
0F3JDXS99V43DZ43CW5NKP496S | 1.10 | 2307251 | 2022-08-26 23:00:42 UTC
0F3JDXW0FM2042R1JA4KTD7Y70 | 4.14 | 2307251 | 2022-08-26 23:00:51 UTC
0F3JDXYQS55A99XFJSHHC6VK32 | 2.33 | 2307251 | 2022-08-26 23:01:00 UTC
0F3JDY1RHGA0DP1P7J8EB6QM92 | 3.23 | 2307251 | 2022-08-26 23:01:10 UTC
0F3JDY4FAJV863B9VA83ERW5M8 | 4.65 | 2307251 | 2022-08-26 23:01:19 UTC
0F3JDY76T0R9D0ZWDP53QZ9VXC | 4.53 | 2307251 | 2022-08-26 23:01:28 UTC
0F3JDYA3ZP7FEXMFMEVQARGDFW | -0.12 | 2307251 | 2022-08-26 23:01:38 UTC
0F3JDYCN2G0T7J8X6ZZWS0Y141 | 9.84 | 2307251 | 2022-08-26 23:01:46 UTC
0F3JDYFC46R7TMZW6BNWXKHW9J | 9.57 | 2307251 | 2022-08-26 23:01:55 UTC
0F3JDYJ35W1VRKP2S4W811NZTK | 5.51 | 2307251 | 2022-08-26 23:02:04 UTC
0F3JDYMTCDRZ3RTV7CHJWFJDAY | 0.82 | 2307251 | 2022-08-26 23:02:13 UTC
0F3JDYQHDBSYHHX0E23Q6SDKT7 | 3.25 | 2307251 | 2022-08-26 23:02:22 UTC
0F3JDYT8GRYTHWHK4M5VY1KYV7 | 3.27 | 2307251 | 2022-08-26 23:02:31 UTC
0F3JDYX45VPWE91DHMJCENYY8D | 4.03 | 2307251 | 2022-08-26 23:02:40 UTC
0F3JDZ0079S28JD4YF5V843RQT | 2.56 | 2307251 | 2022-08-26 23:02:49 UTC
0F3JDZ2RGHWRT2S8BGHGMH30JY | 6.60 | 2307251 | 2022-08-26 23:02:58 UTC
0F3JDZ5ES6XNEWA5J82BBCJQJ0 | 3.51 | 2307251 | 2022-08-26 23:03:07 UTC
0F3JDZ85KT66RP7MYZR5EVJXYR | 4.26 | 2307251 | 2022-08-26 23:03:16 UTC
0F3JDZAX24G8ZWAE7FBTJAHDKB | 4.88 | 2307251 | 2022-08-26 23:03:25 UTC
0F3JDZDM25XT3FS6T1J5C3FTJN | -0.34 | 2307251 | 2022-08-26 23:03:34 UTC
0F3JDZGB6NAB3HPJM3CPN792ZB | 2.47 | 2307251 | 2022-08-26 23:03:43 UTC
0F3JDZK1X6AXCXFD48GMEC4YQF | 3.74 | 2307251 | 2022-08-26 23:03:52 UTC
0F3JDZNSBS4871JRKV2DB876D0 | 0.88 | 2307251 | 2022-08-26 23:04:01 UTC
0F3JDZRGFMPJ49JEXQY1B2E96R | 5.97 | 2307251 | 2022-08-26 23:04:10 UTC
0F3JDZVH39NE291R9EBRQ8ER4F | -1.00 | 2307251 | 2022-08-26 23:04:20 UTC
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

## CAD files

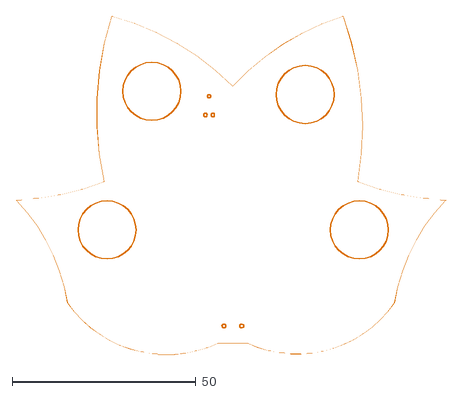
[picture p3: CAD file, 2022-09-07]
CO/PCBs/LeafPCB/EV3/EcobitNRF9160 EV3.dxf
117.0 x 92.1

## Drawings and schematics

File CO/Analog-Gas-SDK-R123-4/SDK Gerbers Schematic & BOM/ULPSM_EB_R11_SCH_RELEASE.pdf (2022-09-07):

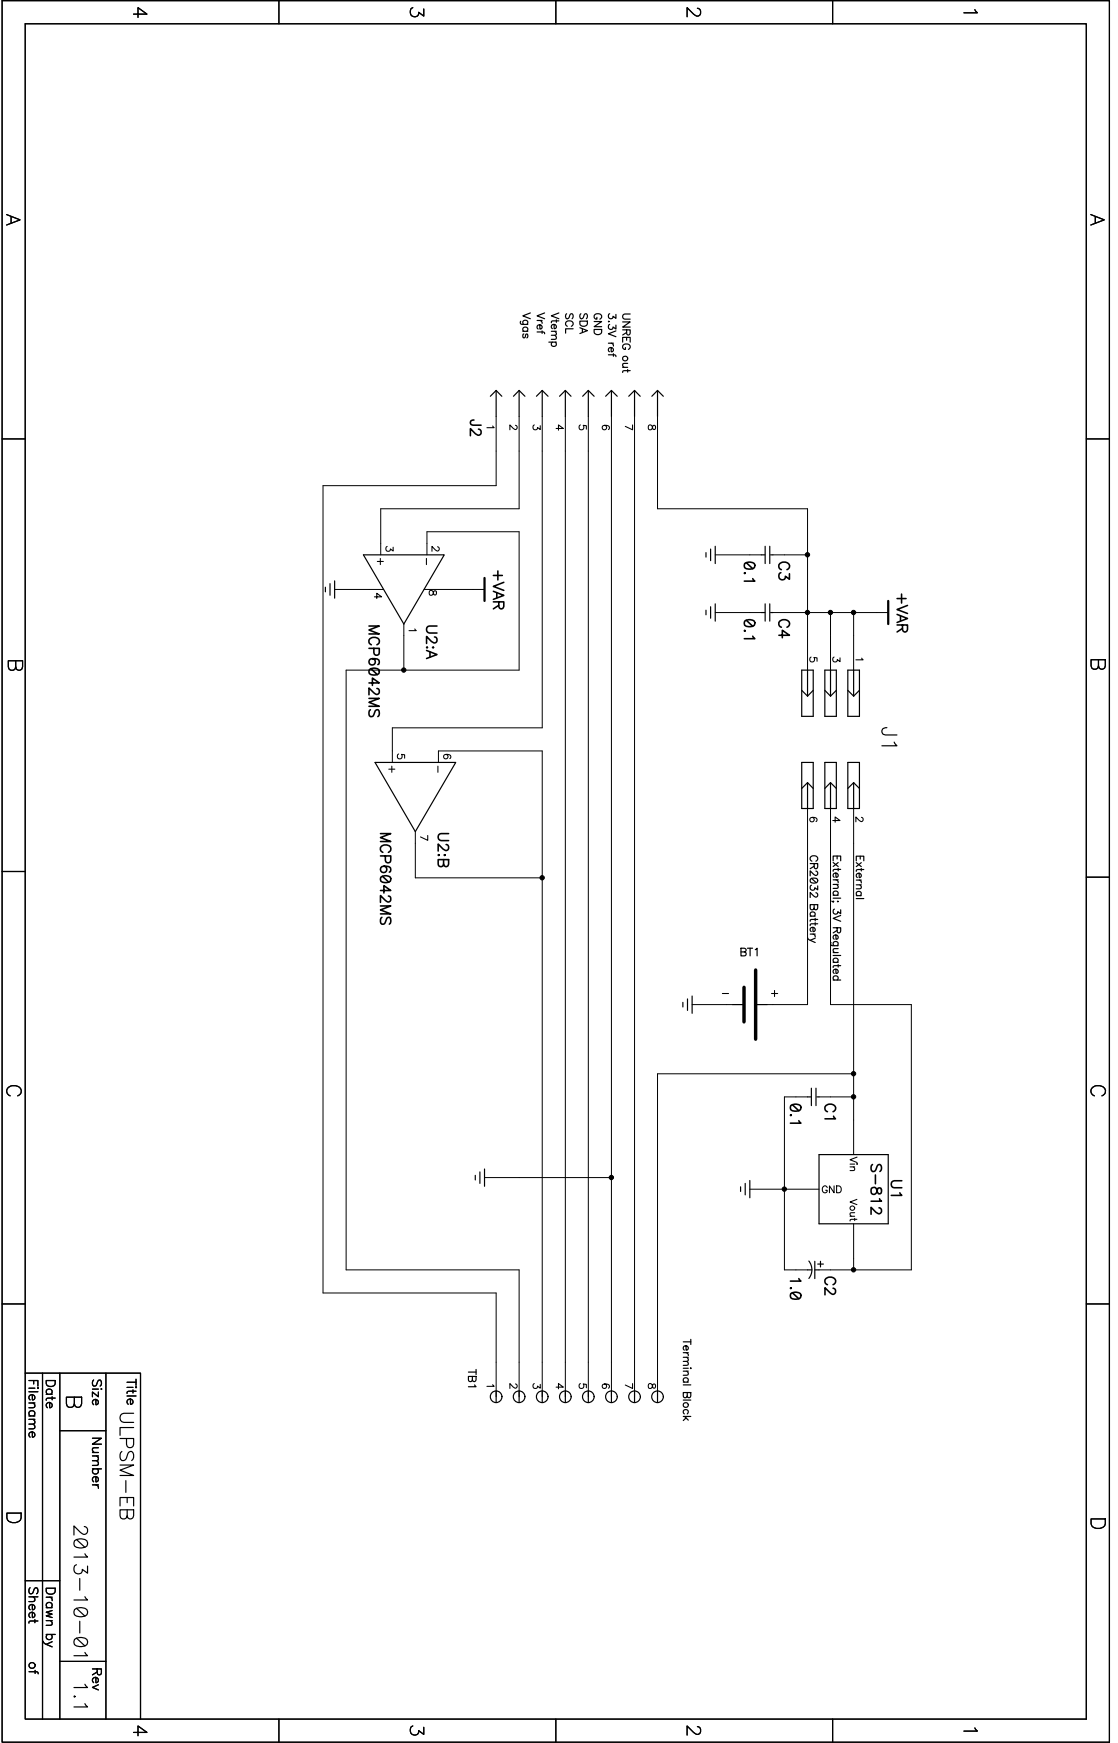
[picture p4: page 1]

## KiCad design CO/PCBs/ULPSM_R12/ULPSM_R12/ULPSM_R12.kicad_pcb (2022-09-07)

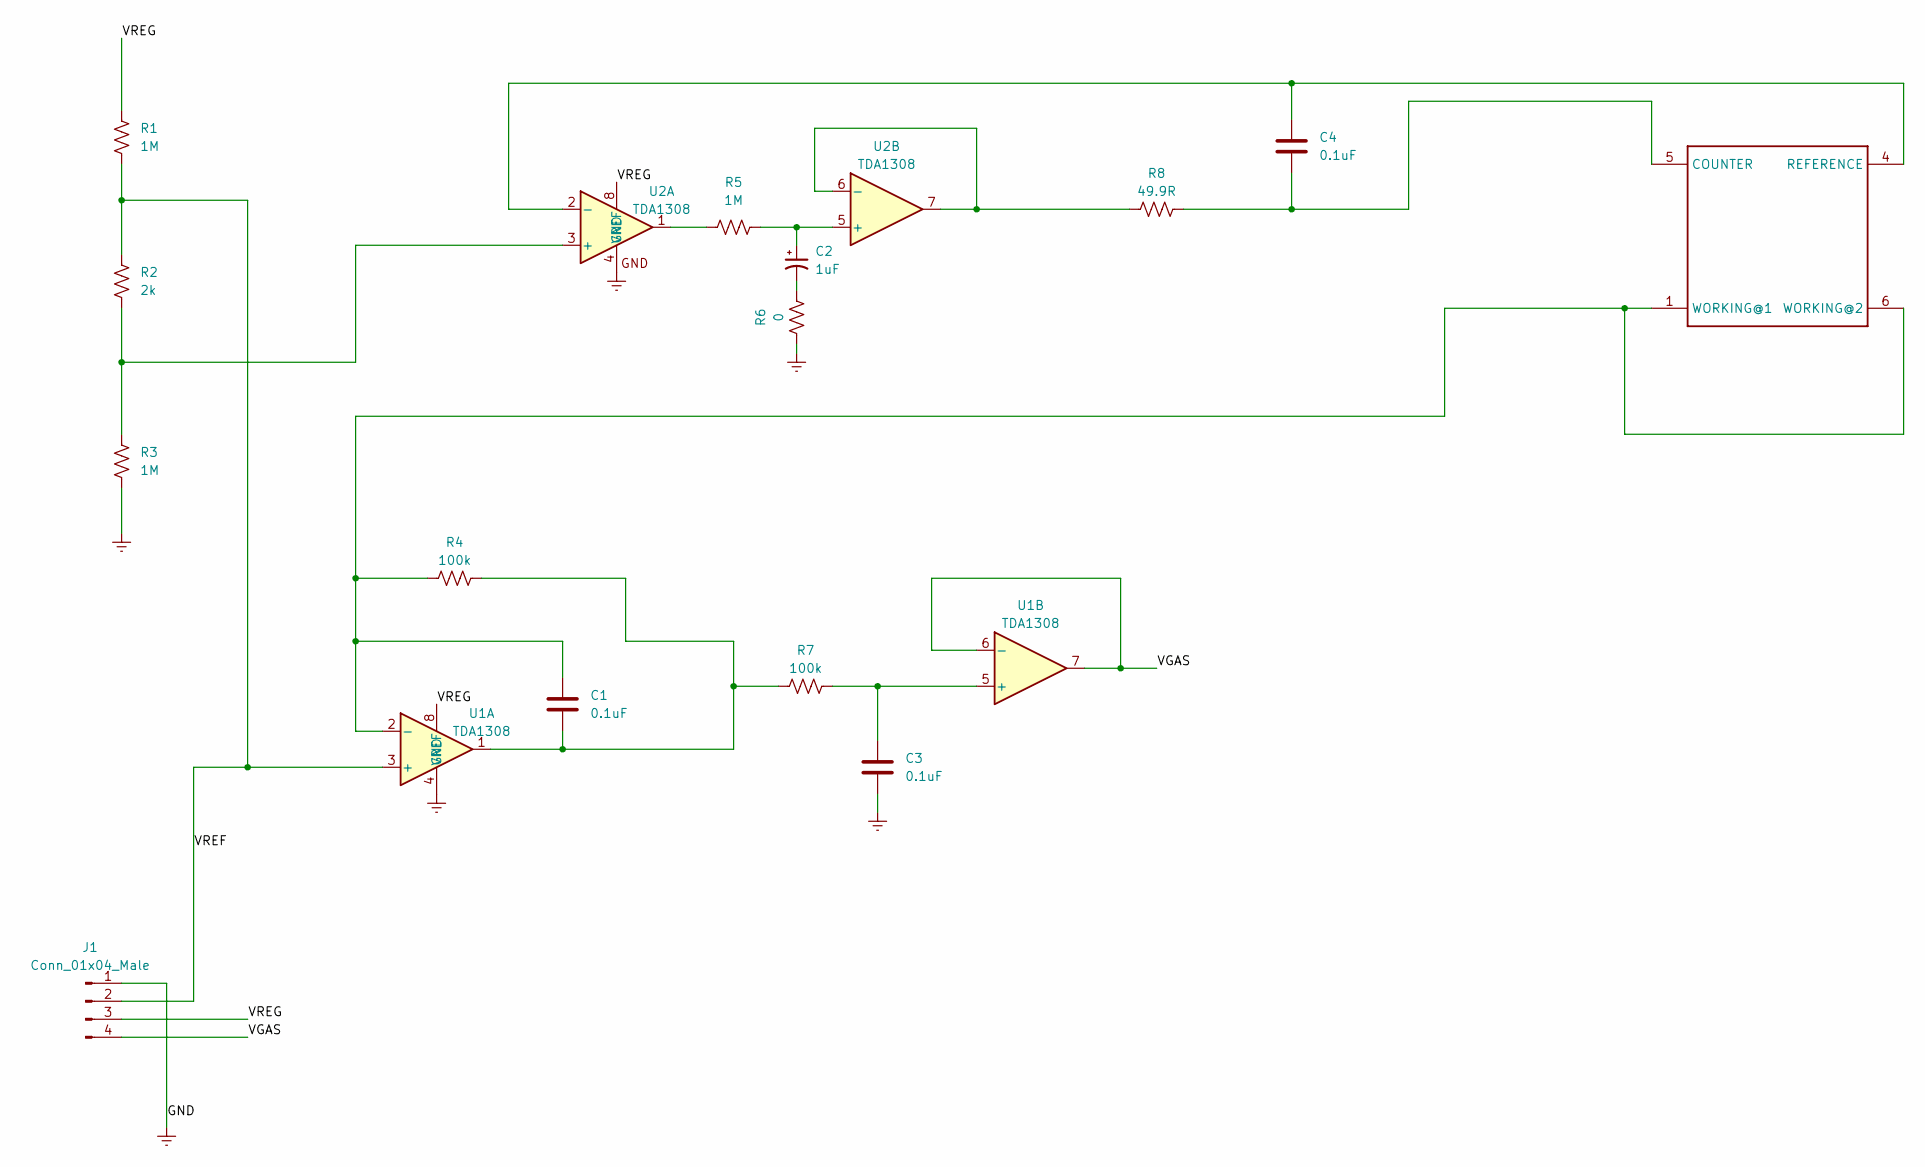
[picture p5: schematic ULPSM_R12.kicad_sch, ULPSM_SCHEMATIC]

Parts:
C1, C3, C4: 0.1uF; C_0805_2012Metric
C2: 1uF; F951E105MPAAQ2
J1: Conn_01x04_Male; PinSocket_1x04_P2.54mm_Vertical
R1, R3, R5: 1M; R_0805_2012Metric
R2: 2k; R_0805_2012Metric
R4, R7: 100k; R_0805_2012Metric
R6: 0; R_0805_2012Metric
R8: 49.9R; R_0805_2012Metric
SENS-CO1: SPECSENSOR; 3SP_CO_1000_P_Package_2
U1, U2: TDA1308; MCP6042T-I&slash_MS

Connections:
/VGAS: J1.4, U1.6 (-), U1.7
/VREF: J1.2, R1.2, R2.1, U1.3 (+)
/VREG: J1.3, R1.1, U1.8 (VREF), U2.8 (VREF)
Earth: C3.2, J1.1, R3.2, R6.1, U1.4 (GND), U2.4 (GND)
unnamed: C1.1, R4.1, SENS-CO1.1 (WORKING@1), SENS-CO1.6 (WORKING@2), U1.2 (-)
unnamed: C1.2, R4.2, R7.1, U1.1
unnamed: C2.1, R5.2, U2.5 (+)
unnamed: C2.2, R6.2
unnamed: C3.1, R7.2, U1.5 (+)
unnamed: C4.1, SENS-CO1.4 (REFERENCE), U2.2 (-)
unnamed: C4.2, R8.2, SENS-CO1.5 (COUNTER)
unnamed: R2.2, R3.1, U2.3 (+)
unnamed: R5.1, U2.1
unnamed: R8.1, U2.6 (-), U2.7

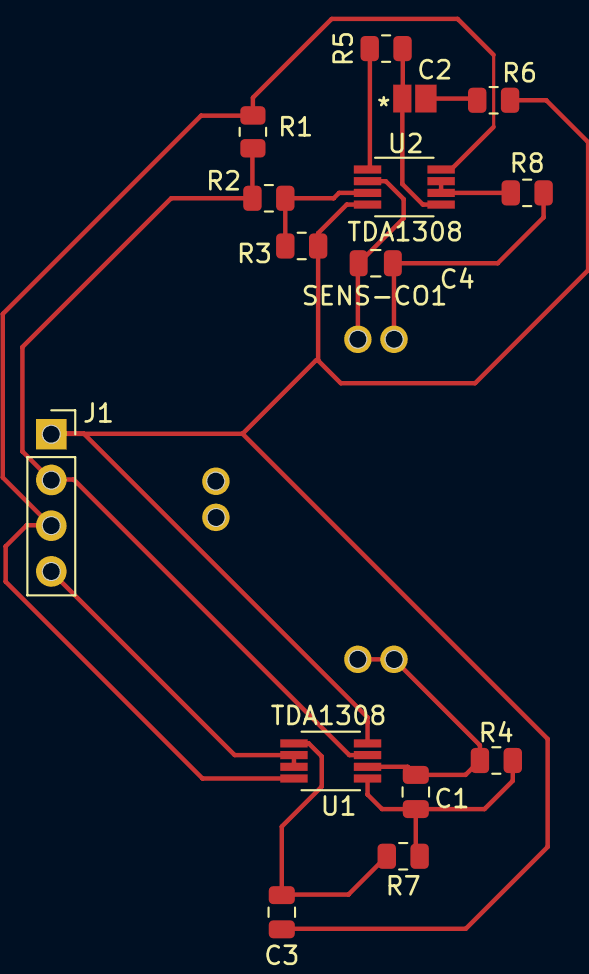
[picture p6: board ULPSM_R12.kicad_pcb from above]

Board: 2 copper layers, 16 parts (0 on the bottom side), 14 nets.

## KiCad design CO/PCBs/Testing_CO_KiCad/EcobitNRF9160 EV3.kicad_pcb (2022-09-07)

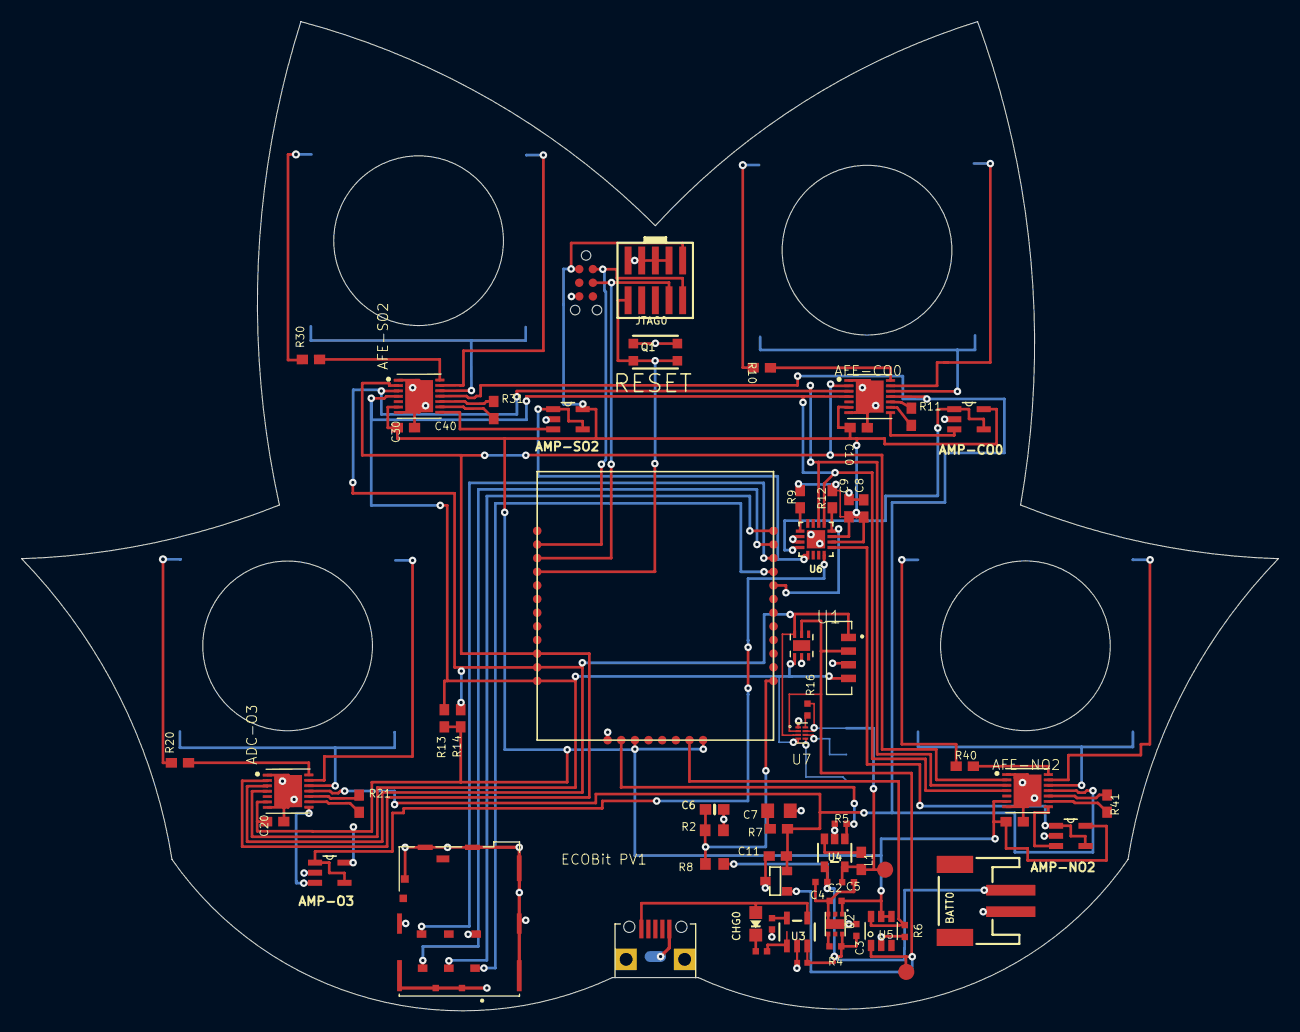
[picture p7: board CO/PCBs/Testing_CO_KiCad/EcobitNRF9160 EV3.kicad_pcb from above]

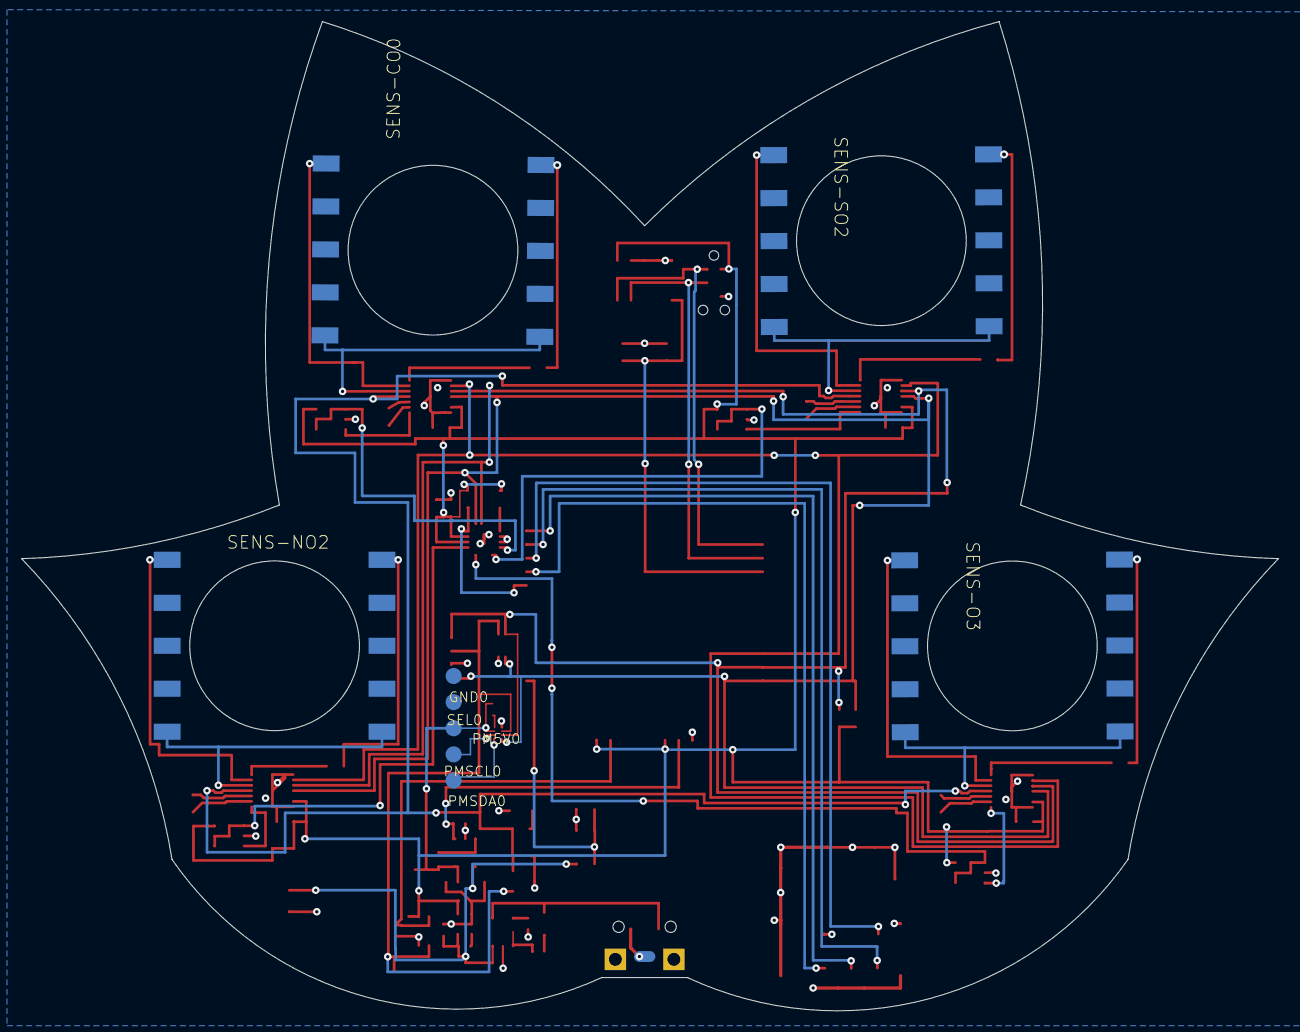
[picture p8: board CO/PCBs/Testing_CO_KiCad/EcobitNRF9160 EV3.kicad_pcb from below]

Board: 4 copper layers, 117.0 x 92.1 mm, 72 parts (9 on the bottom side), 63 nets.

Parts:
ADC-O3: LMP91000SD/NOPB; SON50P400X400X80-15N
AFE-CO0: LMP91000SD/NOPB; SON50P400X400X80-15N
AFE-NO2: LMP91000SD/NOPB; SON50P400X400X80-15N
AFE-SO2: LMP91000SD/NOPB; SON50P400X400X80-15N
AMP-CO0: MCP6041T-E/OT; SOT95P320X145-5N
AMP-NO2: MCP6041T-E/OT; SOT95P320X145-5N
AMP-O3: MCP6041T-E/OT; SOT95P320X145-5N
AMP-SO2: MCP6041T-E/OT; SOT95P320X145-5N
BATT0: 3-6VDC; JSTPH2
C1: 10uF; C-0402
C2, C3, C4, C5: 1uF; RESC0402_N
C6: 1nF; 0603-NO
C7: 10uF 10V 20% Tant; RESC0805_N
C8, C9, C10, C11, C20, C30, C40: 0.1uF; RESC0603_N
CHG0: CHIPLED_0805_NOOUTLINE
GND0: TPTP15R; TP15R
IC1: ISL60002DIH320Z-TK; SOT-23-3
J2: TC2030-MCP-NL
JP1: USB-RECEPTABLE; FCI-10103594-0001LF
JTAG0: 2X05_1.27MM_SMT
L1: 22nH; RESC0603_N
P1: SF72S006VBAR2500; JAE_SF72S006VBAR2500
PM5V0: TPTP15R; TP15R
PMSCL0: TPTP15R; TP15R
PMSDA0: TPTP15R; TP15R
Q1: Btn; BTN_KMR2_4.6X2.8
R1: 10k; R0402
R2: 2M; R0603
R3: 1k; R0402
R4, R5, R6: 10K; RESC0402_N
R7: 1k; RESC0603_N
R8: 806k; R0603
R9, R12: 10k; RESC0603_N
R10, R20, R30, R40: 49.9k; RESC0603_N
R11, R21, R31, R41: 499k; RESC0603_N
R13, R14: 4.7k; RESC0603_N
R16: 200K; RESC0402_N
SEL0: TPTP15R; TP15R
SENS-CO0: SPECSENSOR
SENS-NO2: SPECSENSOR
SENS-O3: SPECSENSOR
SENS-SO2: SPECSENSOR
U1: VEML7700-TR; XDCR_VEML7700-TR
U2: NCP718; NCP718-WDFN6
U3: MCP73831T-2ACI/OT; SOT23-5
U4: AP3418; SOT25
U5: TPS22860DBVR; R-PDSO-G6
U6: ADS122C04; QFN50P300X300X80-16N
U7: PCA9306; PSON35P135X100X50-8N
U$14: HDC1080; TI-S-PWSON-N6
U$35: NRF9160MODULE; NRF9160CASTALLATEDMODULE
UNK5VBUS0, UNK5VBUS1: TPTP15R; TP15R

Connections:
3V3ACC: IC1.1, U1.2, U5.1, U7.2, U$14.5, UNK5VBUS1.TP
3V3EN: R6.2, U5.6, U$35.7
5VBOOSTEN: R5.2, U4.1, U$35.2
5VBUS: C5.2, L1.2, PM5V0.TP, R16.2, U4.5, U7.7, UNK5VBUS0.TP
CO-AMPVOUT: AMP-CO0.1, AMP-CO0.4, U6.4
COVOUT: AFE-CO0.8, AMP-CO0.3
GND: ADC-O3.1, ADC-O3.7, ADC-O3.15, AFE-CO0.1, AFE-CO0.7, AFE-CO0.15, AFE-NO2.1, AFE-NO2.7, AFE-NO2.15, AFE-SO2.1, AFE-SO2.7, AFE-SO2.15, AMP-CO0.2, AMP-NO2.2, AMP-O3.2, AMP-SO2.2, BATT0.1, C1.2, C2.2, C3.2, C4.1, C5.1, C6.1, C7.2, C8.1, C9.1, C10.2, C11.2, C20.2, C30.2, C40.2, GND0.TP, IC1.3, J2.5, JP1.5, JTAG0.3, JTAG0.5, JTAG0.7, JTAG0.9, P1.C5, P1.G1, P1.G2, P1.G3, P1.G4, P1.G5, P1.G6, P1.G7, P1.G8, P1.G9, P1.G10, Q1.B, Q1.B', R1.1, R2.1, R5.1, R6.1, SEL0.TP, U1.3, U2.3, U2.7, U3.2, U4.2, U5.2, U6.2, U6.3, U6.17, U7.1, U$14.2, U$35.1
unnamed: R16.1, U7.8
unnamed: L1.1, U4.3
unnamed: R3.1, U3.1
unnamed: CHG0.C, R3.2
unnamed: AFE-CO0.9, R11.2
unnamed: AFE-CO0.10, R11.1
unnamed: R1.2, U3.5
unnamed: AFE-CO0.14, R10.2
unnamed: C7.1, R7.1
unnamed: ADC-O3.9, R21.2
unnamed: ADC-O3.10, R21.1
unnamed: ADC-O3.14, R20.2
unnamed: AFE-SO2.9, R31.2
unnamed: AFE-SO2.10, R31.1
unnamed: AFE-SO2.14, R30.2
unnamed: AFE-NO2.9, R41.2
unnamed: AFE-NO2.10, R41.1
unnamed: AFE-NO2.14, R40.2
NO2-AMPVOUT: AMP-NO2.1, AMP-NO2.4, U6.9
NO2VOUT: AFE-NO2.8, AMP-NO2.3
O3-AMPVOUT: AMP-O3.1, AMP-O3.4, U6.8
O3VOUT: ADC-O3.8, AMP-O3.3
R-EN: R4.1, U2.4
RESET: JTAG0.10, Q1.A, Q1.A', U$35.29
SCL: ADC-O3.3, AFE-CO0.3, AFE-NO2.3, AFE-SO2.3, R14.1, U1.1, U6.14, U7.3, U$14.6, U$35.22
SCL5V: PMSCL0.TP, U7.6
SDA: ADC-O3.4, AFE-CO0.4, AFE-NO2.4, AFE-SO2.4, R13.1, U1.4, U6.13, U7.4, U$14.1, U$35.21
SDA5V: PMSDA0.TP, U7.5
SIM1V8: P1.C1, U$35.17
SIMCLK: P1.C3, U$35.19
SIMIO: P1.C7, U$35.18
SIMRESET: P1.C2, U$35.20
SO2-AMPVOUT: AMP-SO2.1, AMP-SO2.4, U6.5
SO2VOUT: AFE-SO2.8, AMP-SO2.3
SPEC-CO-COUNTER: R10.1, SENS-CO0.6
SPEC-CO-REF: AFE-CO0.13, SENS-CO0.5
SPEC-CO-WKG: AFE-CO0.12, SENS-CO0.1, SENS-CO0.10
SPEC-NO2-COUNTER: R40.1, SENS-NO2.6
SPEC-NO2-REF: AFE-NO2.13, SENS-NO2.5
SPEC-NO2-WKG: AFE-NO2.12, SENS-NO2.1, SENS-NO2.10
SPEC-O3-COUNTER: R20.1, SENS-O3.6
SPEC-O3-REF: ADC-O3.13, SENS-O3.5
SPEC-O3-WKG: ADC-O3.12, SENS-O3.1, SENS-O3.10
SPEC-SO2-COUNTER: R30.1, SENS-SO2.6
SPEC-SO2-REF: AFE-SO2.13, SENS-SO2.5
SPEC-SO2-WKG: AFE-SO2.12, SENS-SO2.1, SENS-SO2.10
SWCLK: J2.4, JTAG0.4, U$35.30
SWDIO: J2.2, JTAG0.2, U$35.31
VBAT: BATT0.2, C1.1, C3.1, C4.2, R4.2, R8.2, U2.6, U3.3, U4.4
VBUS: CHG0.A, JP1.1, U3.4
VDD: ADC-O3.6, AFE-CO0.6, AFE-NO2.6, AFE-SO2.6, AMP-CO0.5, AMP-NO2.5, AMP-O3.5, AMP-SO2.5, C2.1, C8.2, C9.2, C10.1, C20.1, C30.1, C40.1, J2.1, JTAG0.1, R9.2, R12.2, R13.2, R14.2, U2.1, U5.4, U5.5, U6.10, U6.11, U$35.3, U$35.8
VDIV: C6.2, R2.2, R8.1, U$35.9
VREFADC: ADC-O3.11, AFE-CO0.11, AFE-NO2.11, AFE-SO2.11, C11.1, IC1.2, R7.2
~DRDY: R12.1, U6.12, U$35.16
~GASSENS-EN: ADC-O3.2, AFE-CO0.2, AFE-NO2.2, AFE-SO2.2, U$35.23
~RESET: R9.1, U6.1

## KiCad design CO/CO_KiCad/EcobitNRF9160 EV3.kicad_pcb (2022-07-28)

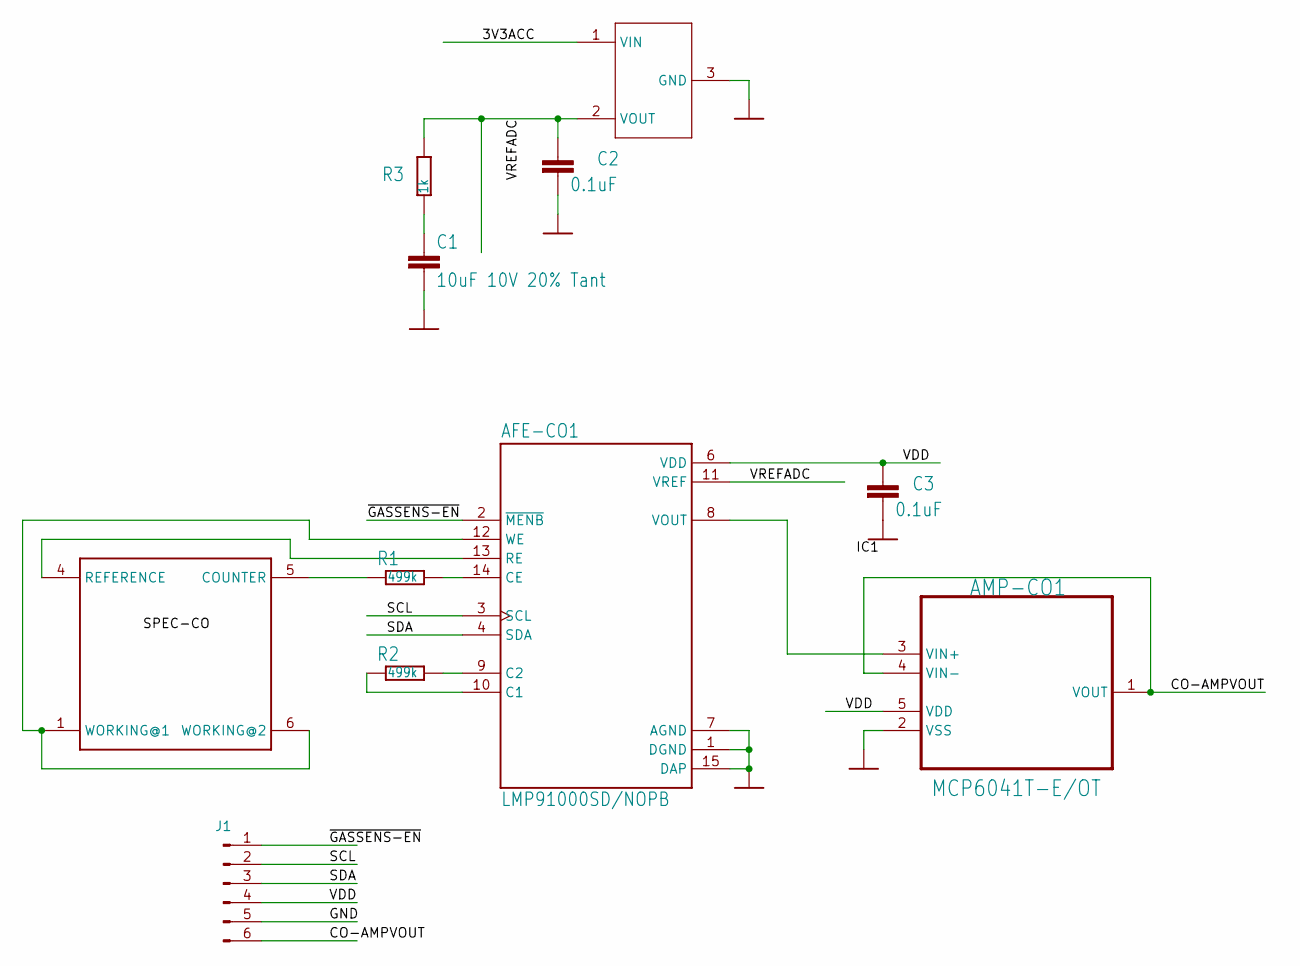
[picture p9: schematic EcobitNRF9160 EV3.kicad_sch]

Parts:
AFE-CO1: LMP91000SD/NOPB; SON50P400X400X80-15N
AMP-CO1: MCP6041T-E/OT; SOT95P320X145-5N
C1: 10uF 10V 20% Tant; RESC0805_N
C2, C3: 0.1uF; RESC0603_N
IC1: ISL60002DIH320Z-TK; SOT-23-3
J1: Conn_01x06_Male; PinSocket_1x06_P2.54mm_Vertical
R1, R2: 499k; RESC0603_N
R3: 1k; RESC0603_N
SENS-CO1: SPECSENSOR; 3SP_CO_1000_P_Package_2

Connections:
/3V3ACC: IC1.1 (VIN)
/CO-AMPVOUT: AMP-CO1.1 (VOUT), AMP-CO1.4 (VIN-), J1.6
/SCL: AFE-CO1.3 (SCL), J1.2
/SDA: AFE-CO1.4 (SDA), J1.3
/VDD: AFE-CO1.6 (VDD), AMP-CO1.5 (VDD), C3.1, J1.4
/VREFADC: AFE-CO1.11 (VREF), C2.1, IC1.2 (VOUT), R3.2
/~GASSENS-EN: AFE-CO1.2 (~MENB), J1.1
GND: AFE-CO1.1 (DGND), AFE-CO1.7 (AGND), AFE-CO1.15 (DAP), AMP-CO1.2 (VSS), C1.2, C2.2, C3.2, IC1.3 (GND), J1.5
unnamed: AFE-CO1.8 (VOUT), AMP-CO1.3 (VIN+)
unnamed: AFE-CO1.9 (C2), R2.2
unnamed: AFE-CO1.10 (C1), R2.1
unnamed: AFE-CO1.12 (WE), SENS-CO1.1 (WORKING@1), SENS-CO1.6 (WORKING@2)
unnamed: AFE-CO1.13 (RE), SENS-CO1.4 (REFERENCE)
unnamed: AFE-CO1.14 (CE), R1.2
unnamed: C1.1, R3.1
unnamed: R1.1, SENS-CO1.5 (COUNTER)

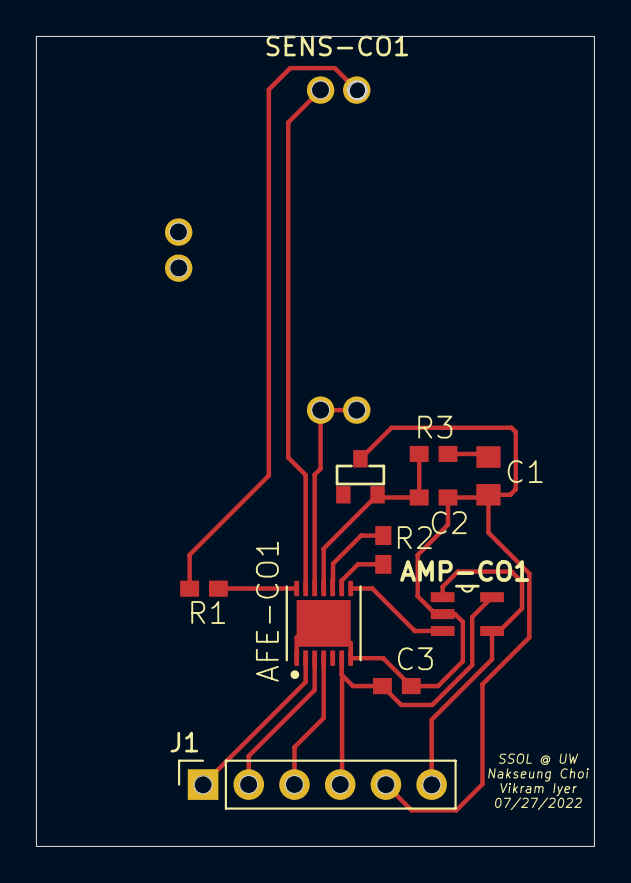
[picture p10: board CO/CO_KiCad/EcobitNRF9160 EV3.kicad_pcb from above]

Board: 4 copper layers, 31.0 x 45.0 mm, 11 parts (0 on the bottom side), 15 nets.

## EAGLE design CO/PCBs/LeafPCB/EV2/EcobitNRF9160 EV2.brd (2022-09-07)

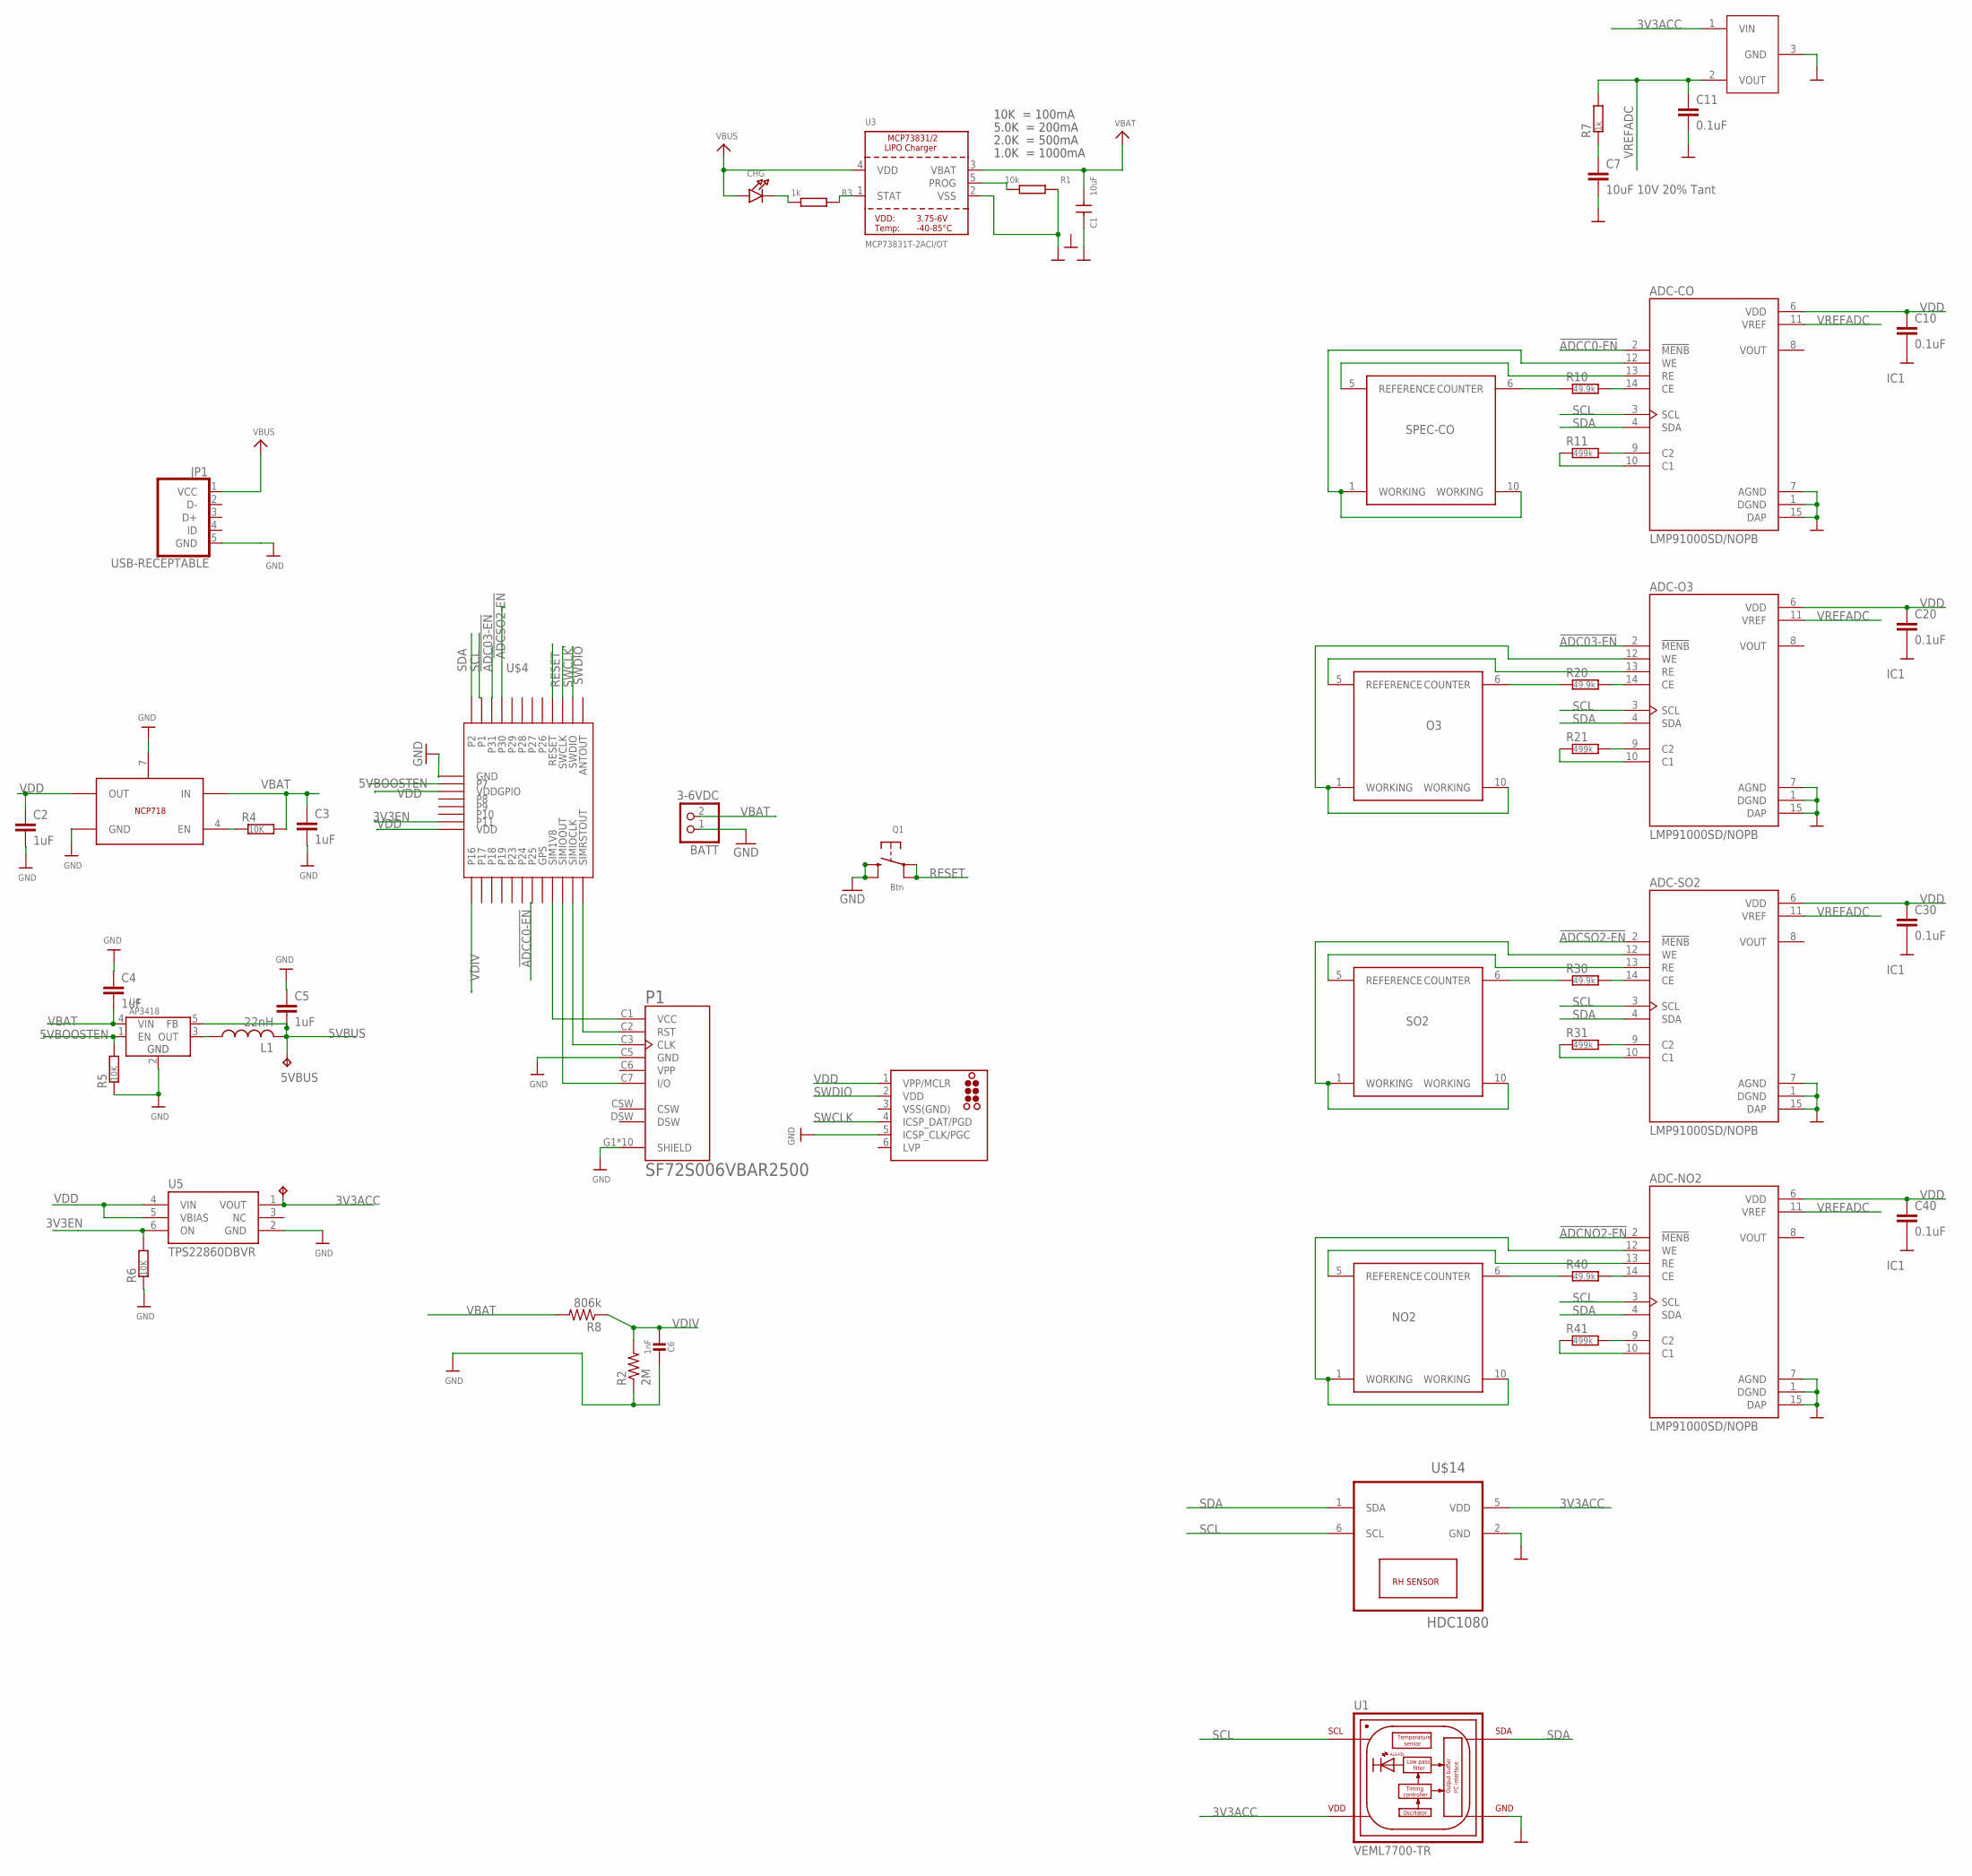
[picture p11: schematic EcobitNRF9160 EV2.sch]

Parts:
5VBUS, 5VBUS1: TPTP15R; TP15R
ADC-CO: LMP91000SD/NOPB; SON50P400X400X80-15N
ADC-NO2: LMP91000SD/NOPB; SON50P400X400X80-15N
ADC-O3: LMP91000SD/NOPB; SON50P400X400X80-15N
ADC-SO2: LMP91000SD/NOPB; SON50P400X400X80-15N
BATT: 3-6VDC; JSTPH2
C1: 10uF; C-0402
C2, C3, C4, C5: 1uF; RESC0402_N
C6: 1nF; 0603-NO
C7: 10uF 10V 20% Tant; RESC0805_N
C10, C11, C20, C30, C40: 0.1uF; RESC0603_N
CHG: LED0805_NOOUTLINE; CHIPLED_0805_NOOUTLINE
IC1: ISL60002DIH320Z-TK; SOT-23-3
J2: TC2030-MCP-NL
JP1: USB-RECEPTABLE; FCI-10103594-0001LF
L1: 22nH; RESC0603_N
NO2: SPECSENSOR
O3: SPECSENSOR
P1: SF72S006VBAR2500; JAE_SF72S006VBAR2500
Q1: Btn; BTN_KMR2_4.6X2.8
R1: 10k; R0402
R2: 2M; R0603
R3: 1k; R0402
R4, R5, R6: 10K; RESC0402_N
R7: 1k; RESC0603_N
R8: 806k; R0603
R10, R20, R30, R40: 49.9k; RESC0603_N
R11, R21, R31, R41: 499k; RESC0603_N
SO2: SPECSENSOR
SPEC-CO: SPECSENSOR
U1: VEML7700-TR; XDCR_VEML7700-TR
U2: NCP718; NCP718-WDFN6
U3: MCP73831T-2ACI/OT; SOT23-5
U4: AP3418; SOT25
U5: TPS22860DBVR; R-PDSO-G6
U$4: NRF9160MODULE
U$14: HDC1080; TI-S-PWSON-N6

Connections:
3V3ACC: 5VBUS1.TP, IC1.1 (VIN), U1.2 (VDD), U5.1 (VOUT), U$14.5 (VDD)
3V3EN: R6.2, U5.6 (ON), U$4.P11
5VBOOSTEN: R5.2, U4.1 (EN), U$4.P7
5VBUS: 5VBUS.TP, C5.2, L1.2, U4.5 (FB)
!ADC03-EN: ADC-O3.2 (!MENB), U$4.P31
!ADCC0-EN: ADC-CO.2 (!MENB), U$4.P25
!ADCNO2-EN: ADC-NO2.2 (!MENB)
!ADCSO2-EN: ADC-SO2.2 (!MENB), U$4.P30
GND: ADC-CO.1 (DGND), ADC-CO.7 (AGND), ADC-CO.15 (DAP), ADC-NO2.1 (DGND), ADC-NO2.7 (AGND), ADC-NO2.15 (DAP), ADC-O3.1 (DGND), ADC-O3.7 (AGND), ADC-O3.15 (DAP), ADC-SO2.1 (DGND), ADC-SO2.7 (AGND), ADC-SO2.15 (DAP), BATT.1, C1.2, C2.2, C3.2, C4.1, C5.1, C6.1, C7.2, C10.2, C11.2, C20.2, C30.2, C40.2, IC1.3 (GND), J2.5 (ICSP_CLK/PGC), JP1.5 (GND), P1.C5 (GND), P1.G1 (SHIELD), P1.G2 (SHIELD), P1.G3 (SHIELD), P1.G4 (SHIELD), P1.G5 (SHIELD), P1.G6 (SHIELD), P1.G7 (SHIELD), P1.G8 (SHIELD), P1.G9 (SHIELD), P1.G10 (SHIELD), Q1.B (S), Q1.B' (S1), R1.1, R2.1, R5.1, R6.1, U1.3 (GND), U2.3 (GND), U2.7 (GND), U3.2 (VSS), U4.2 (GND), U5.2 (GND), U$4.GND, U$14.2 (GND)
unnamed: P1.C1 (VCC), U$4.SIM1V8
unnamed: L1.1, U4.3 (OUT)
unnamed: R3.1, U3.1 (STAT)
unnamed: CHG.C, R3.2
unnamed: P1.C2 (RST), U$4.SIMRSTOUT
unnamed: P1.C3 (CLK), U$4.SIMCLKOUT (SIMIOCLK)
unnamed: P1.C7 (I/O), U$4.SIMIOOUT
unnamed: ADC-CO.9 (C2), R11.2
unnamed: ADC-CO.10 (C1), R11.1
unnamed: R1.2, U3.5 (PROG)
unnamed: ADC-CO.14 (CE), R10.2
unnamed: C7.1, R7.1
unnamed: ADC-O3.9 (C2), R21.2
unnamed: ADC-O3.10 (C1), R21.1
unnamed: ADC-O3.14 (CE), R20.2
unnamed: ADC-SO2.9 (C2), R31.2
unnamed: ADC-SO2.10 (C1), R31.1
unnamed: ADC-SO2.14 (CE), R30.2
unnamed: ADC-NO2.9 (C2), R41.2
unnamed: ADC-NO2.10 (C1), R41.1
unnamed: ADC-NO2.14 (CE), R40.2
R-EN: R4.1, U2.4 (EN)
RESET: Q1.A, Q1.A' (P1), U$4.RESET
SCL: ADC-CO.3 (SCL), ADC-NO2.3 (SCL), ADC-O3.3 (SCL), ADC-SO2.3 (SCL), U1.1 (SCL), U$4.P1, U$14.6 (SCL)
SDA: ADC-CO.4 (SDA), ADC-NO2.4 (SDA), ADC-O3.4 (SDA), ADC-SO2.4 (SDA), U1.4 (SDA), U$4.P2, U$14.1 (SDA)
SPEC-CO-COUNTER: R10.1, SPEC-CO.6 (COUNTER)
SPEC-CO-REF: ADC-CO.13 (RE), SPEC-CO.5 (REFERENCE)
SPEC-CO-WKG: ADC-CO.12 (WE), SPEC-CO.1 (WORKING), SPEC-CO.10 (WORKING)
SPEC-NO2-COUNTER: NO2.6 (COUNTER), R40.1
SPEC-NO2-REF: ADC-NO2.13 (RE), NO2.5 (REFERENCE)
SPEC-NO2-WKG: ADC-NO2.12 (WE), NO2.1 (WORKING), NO2.10 (WORKING)
SPEC-O3-COUNTER: O3.6 (COUNTER), R20.1
SPEC-O3-REF: ADC-O3.13 (RE), O3.5 (REFERENCE)
SPEC-O3-WKG: ADC-O3.12 (WE), O3.1 (WORKING), O3.10 (WORKING)
SPEC-SO2-COUNTER: R30.1, SO2.6 (COUNTER)
SPEC-SO2-REF: ADC-SO2.13 (RE), SO2.5 (REFERENCE)
SPEC-SO2-WKG: ADC-SO2.12 (WE), SO2.1 (WORKING), SO2.10 (WORKING)
SWCLK: J2.4 (ICSP_DAT/PGD), U$4.SWCLK
SWDIO: J2.2 (VDD), U$4.SWDIO
VBAT: BATT.2, C1.1, C3.1, C4.2, R4.2, R8.2, U2.6 (IN), U3.3 (VBAT), U4.4 (VIN)
VBUS: CHG.A, JP1.1 (VCC), U3.4 (VDD)
VDD: ADC-CO.6 (VDD), ADC-NO2.6 (VDD), ADC-O3.6 (VDD), ADC-SO2.6 (VDD), C2.1, C10.1, C20.1, C30.1, C40.1, J2.1 (VPP/MCLR), U2.1 (OUT), U5.4 (VIN), U5.5 (VBIAS), U$4.VDD, U$4.VDDGPIO
VDIV: C6.2, R2.2, R8.1, U$4.P16
VPP: P1.C6 (VPP)
VREFADC: ADC-CO.11 (VREF), ADC-NO2.11 (VREF), ADC-O3.11 (VREF), ADC-SO2.11 (VREF), C11.1, IC1.2 (VOUT), R7.2
VSS(GND): J2.3 (VSS(GND))

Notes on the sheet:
10K = 100mA
5.0K = 200mA
2.0K = 500mA
1.0K = 1000mA

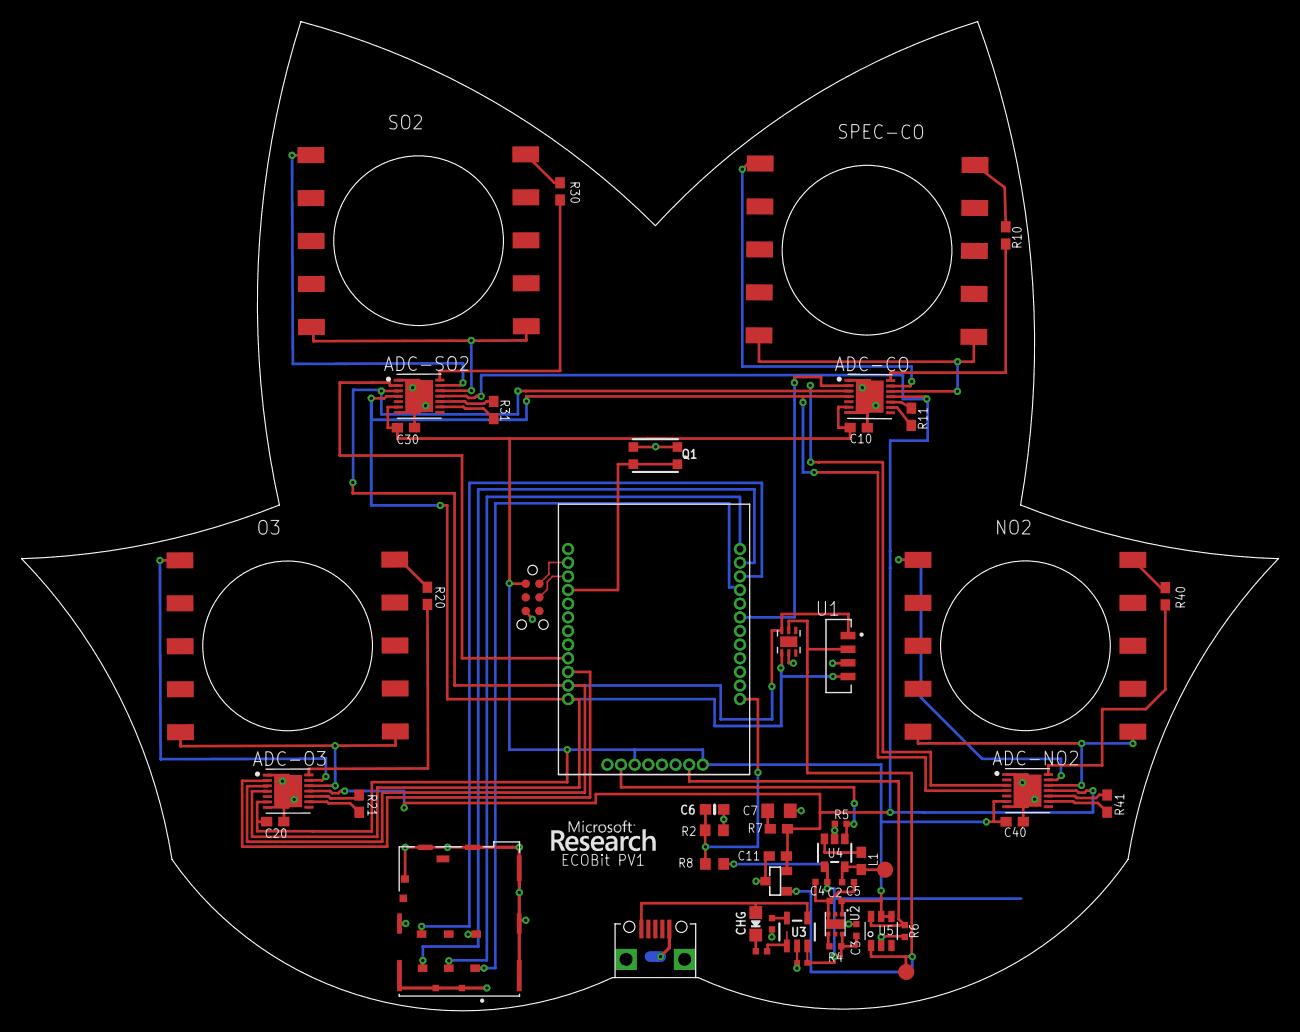
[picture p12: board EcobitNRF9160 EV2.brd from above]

Board: 2 copper layers, 117.0 x 92.1 mm, 53 parts (1 on the bottom side), 52 nets.

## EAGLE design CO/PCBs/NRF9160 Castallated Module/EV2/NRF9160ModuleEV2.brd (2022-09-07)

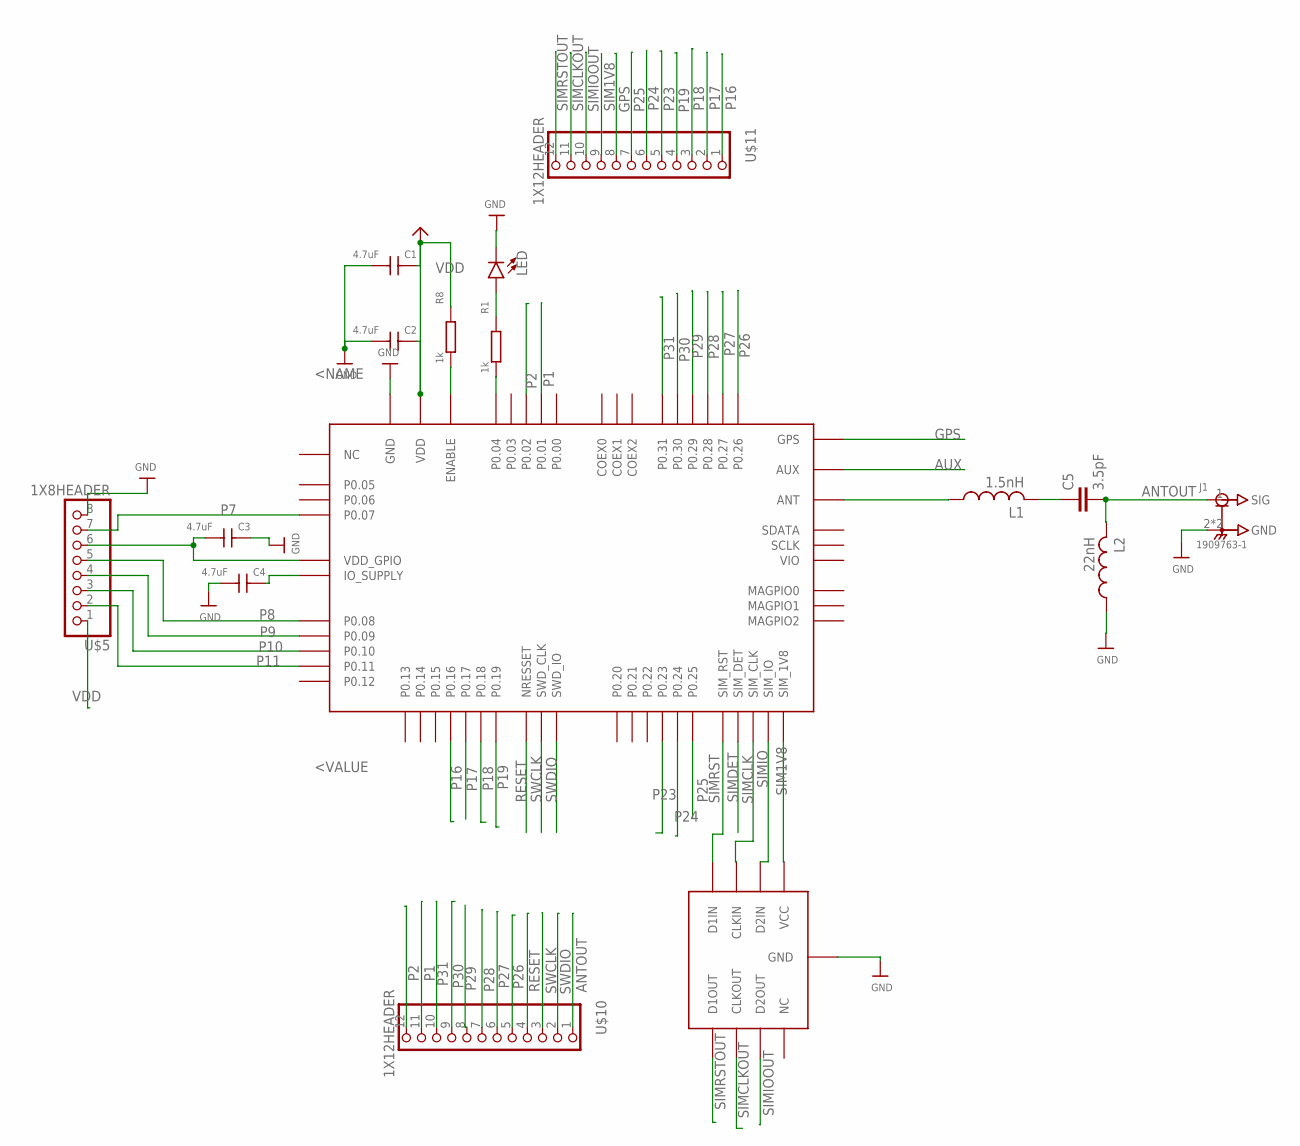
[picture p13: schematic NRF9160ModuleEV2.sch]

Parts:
C1, C2, C3, C4: 4.7uF; C-0402
C5: 3.5pF; RESC0402_N
IC1: NRF9160
J1: 1909763-1; TE_1909763-1
L1: 1.5nH; RESC0603_N
L2: 22nH; RESC0603_N
LED: LED0603; LED-0603
R1, R8: 1k; R0402
U1: TPD3F303; 8-UFDFN
U$5: 1X8HEADER; 8X1
U$10, U$11: 1X12HEADER; 1X12

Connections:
ANTOUT: C5.2, J1.1 (SIG), L2.2, U$10.1
AUX: IC1.AUX
GND: C1.1, C2.1, C3.2, C4.1, IC1.GND@1 (GND), IC1.GND@2 (GND), IC1.GND@3 (GND), IC1.GND@4 (GND), IC1.GND@5 (GND), IC1.GND@6 (GND), IC1.GND@7 (GND), IC1.GND@8 (GND), IC1.GND@9 (GND), IC1.GND@10 (GND), IC1.GND@11 (GND), IC1.GND@12 (GND), IC1.GND@13 (GND), IC1.GND@14 (GND), IC1.GND@15 (GND), IC1.GND@16 (GND), IC1.GND@17 (GND), IC1.GND@18 (GND), IC1.GND@19 (GND), IC1.GND@20 (GND), IC1.GND@21 (GND), IC1.GND@22 (GND), IC1.GND@23 (GND), IC1.GND@24 (GND), IC1.GND@25 (GND), IC1.GND@26 (GND), IC1.GND@27 (GND), IC1.GND@28 (GND), IC1.GND@29 (GND), IC1.GND@30 (GND), IC1.GND@31 (GND), IC1.GND@32 (GND), IC1.GND@33 (GND), IC1.GND@34 (GND), IC1.GND@35 (GND), IC1.GND_SHIELD@1 (GND), IC1.GND_SHIELD@2 (GND), IC1.GND_SHIELD@3 (GND), IC1.GND_SHIELD@4 (GND), IC1.GND_SHIELD@5 (GND), IC1.GND_SHIELD@6 (GND), IC1.GND_SHIELD@7 (GND), IC1.GND_SHIELD@8 (GND), IC1.GND_SHIELD@9 (GND), IC1.GND_SHIELD@10 (GND), IC1.GND_SHIELD@11 (GND), IC1.GND_SHIELD@12 (GND), IC1.GND_SHIELD@13 (GND), IC1.GND_SHIELD@14 (GND), IC1.GND_SHIELD@15 (GND), IC1.GND_SHIELD@16 (GND), IC1.GND_SHIELD@17 (GND), IC1.GND_SHIELD@18 (GND), IC1.GND_SHIELD@19 (GND), IC1.GND_SHIELD@20 (GND), IC1.GND_SHIELD@21 (GND), IC1.GND_SHIELD@22 (GND), IC1.GND_SHIELD@23 (GND), IC1.GND_SHIELD@24 (GND), IC1.GND_SHIELD@25 (GND), IC1.GND_SHIELD@26 (GND), IC1.GND_SHIELD@27 (GND), IC1.GND_SHIELD@28 (GND), IC1.GND_SHIELD@29 (GND), IC1.GND_SHIELD@30 (GND), IC1.GND_SHIELD@31 (GND), IC1.GND_SHIELD@32 (GND), IC1.GND_SHIELD@33 (GND), IC1.GND_SHIELD@34 (GND), J1.2 (GND), J1.3 (GND), L2.1, LED.C, U1.P$9 (GND), U$5.8
GPS: IC1.GPS, U$11.8
unnamed: IC1.ENABLE, R8.2
unnamed: C4.2, IC1.IO_SUPPLY
unnamed: C3.1, IC1.VDD_GPIO, U$5.6
unnamed: IC1.P0.04, R1.2
unnamed: LED.A, R1.1
unnamed: IC1.ANT, L1.1
unnamed: C5.1, L1.2
P1: IC1.P0.01, U$10.11
P2: IC1.P0.02, U$10.12
P7: IC1.P0.07, U$5.7
P8: IC1.P0.08, U$5.5
P9: IC1.P0.09, U$5.4
P10: IC1.P0.10, U$5.3
P11: IC1.P0.11, U$5.2
P16: IC1.P0.16, U$11.1
P17: IC1.P0.17, U$11.2
P18: IC1.P0.18, U$11.3
P19: IC1.P0.19, U$11.4
P23: IC1.P0.23, U$11.5
P24: IC1.P0.24, U$11.6
P25: IC1.P0.25, U$11.7
P26: IC1.P0.26, U$10.5
P27: IC1.P0.27, U$10.6
P28: IC1.P0.28, U$10.7
P29: IC1.P0.29, U$10.8
P30: IC1.P0.30, U$10.9
P31: IC1.P0.31, U$10.10
RESET: IC1.NRESET (NRESSET), U$10.4
SIM1V8: IC1.SIM_1V8, U1.VCC, U$11.9
SIMCLK: IC1.SIM_CLK, U1.CLKIN
SIMCLKOUT: U1.CLKOUT, U$11.11
SIMDET: IC1.SIM_DET
SIMIO: IC1.SIM_IO, U1.D2IN
SIMIOOUT: U1.D2OUT, U$11.10
SIMRST: IC1.SIM_RST, U1.D1IN
SIMRSTOUT: U1.D1OUT, U$11.12
SWCLK: IC1.SWDCLK (SWD_CLK), U$10.3
SWDIO: IC1.SWDIO (SWD_IO), U$10.2
VDD: C1.2, C2.2, IC1.VDD@1 (VDD), IC1.VDD@2 (VDD), R8.1, U$5.1

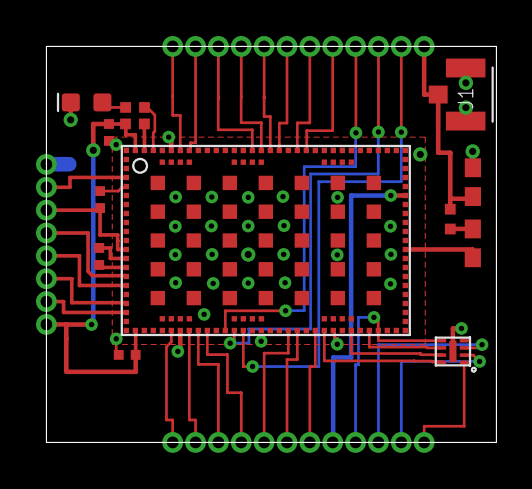
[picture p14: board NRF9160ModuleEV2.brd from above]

Board: 2 copper layers, 25.0 x 22.0 mm, 16 parts (0 on the bottom side), 41 nets.

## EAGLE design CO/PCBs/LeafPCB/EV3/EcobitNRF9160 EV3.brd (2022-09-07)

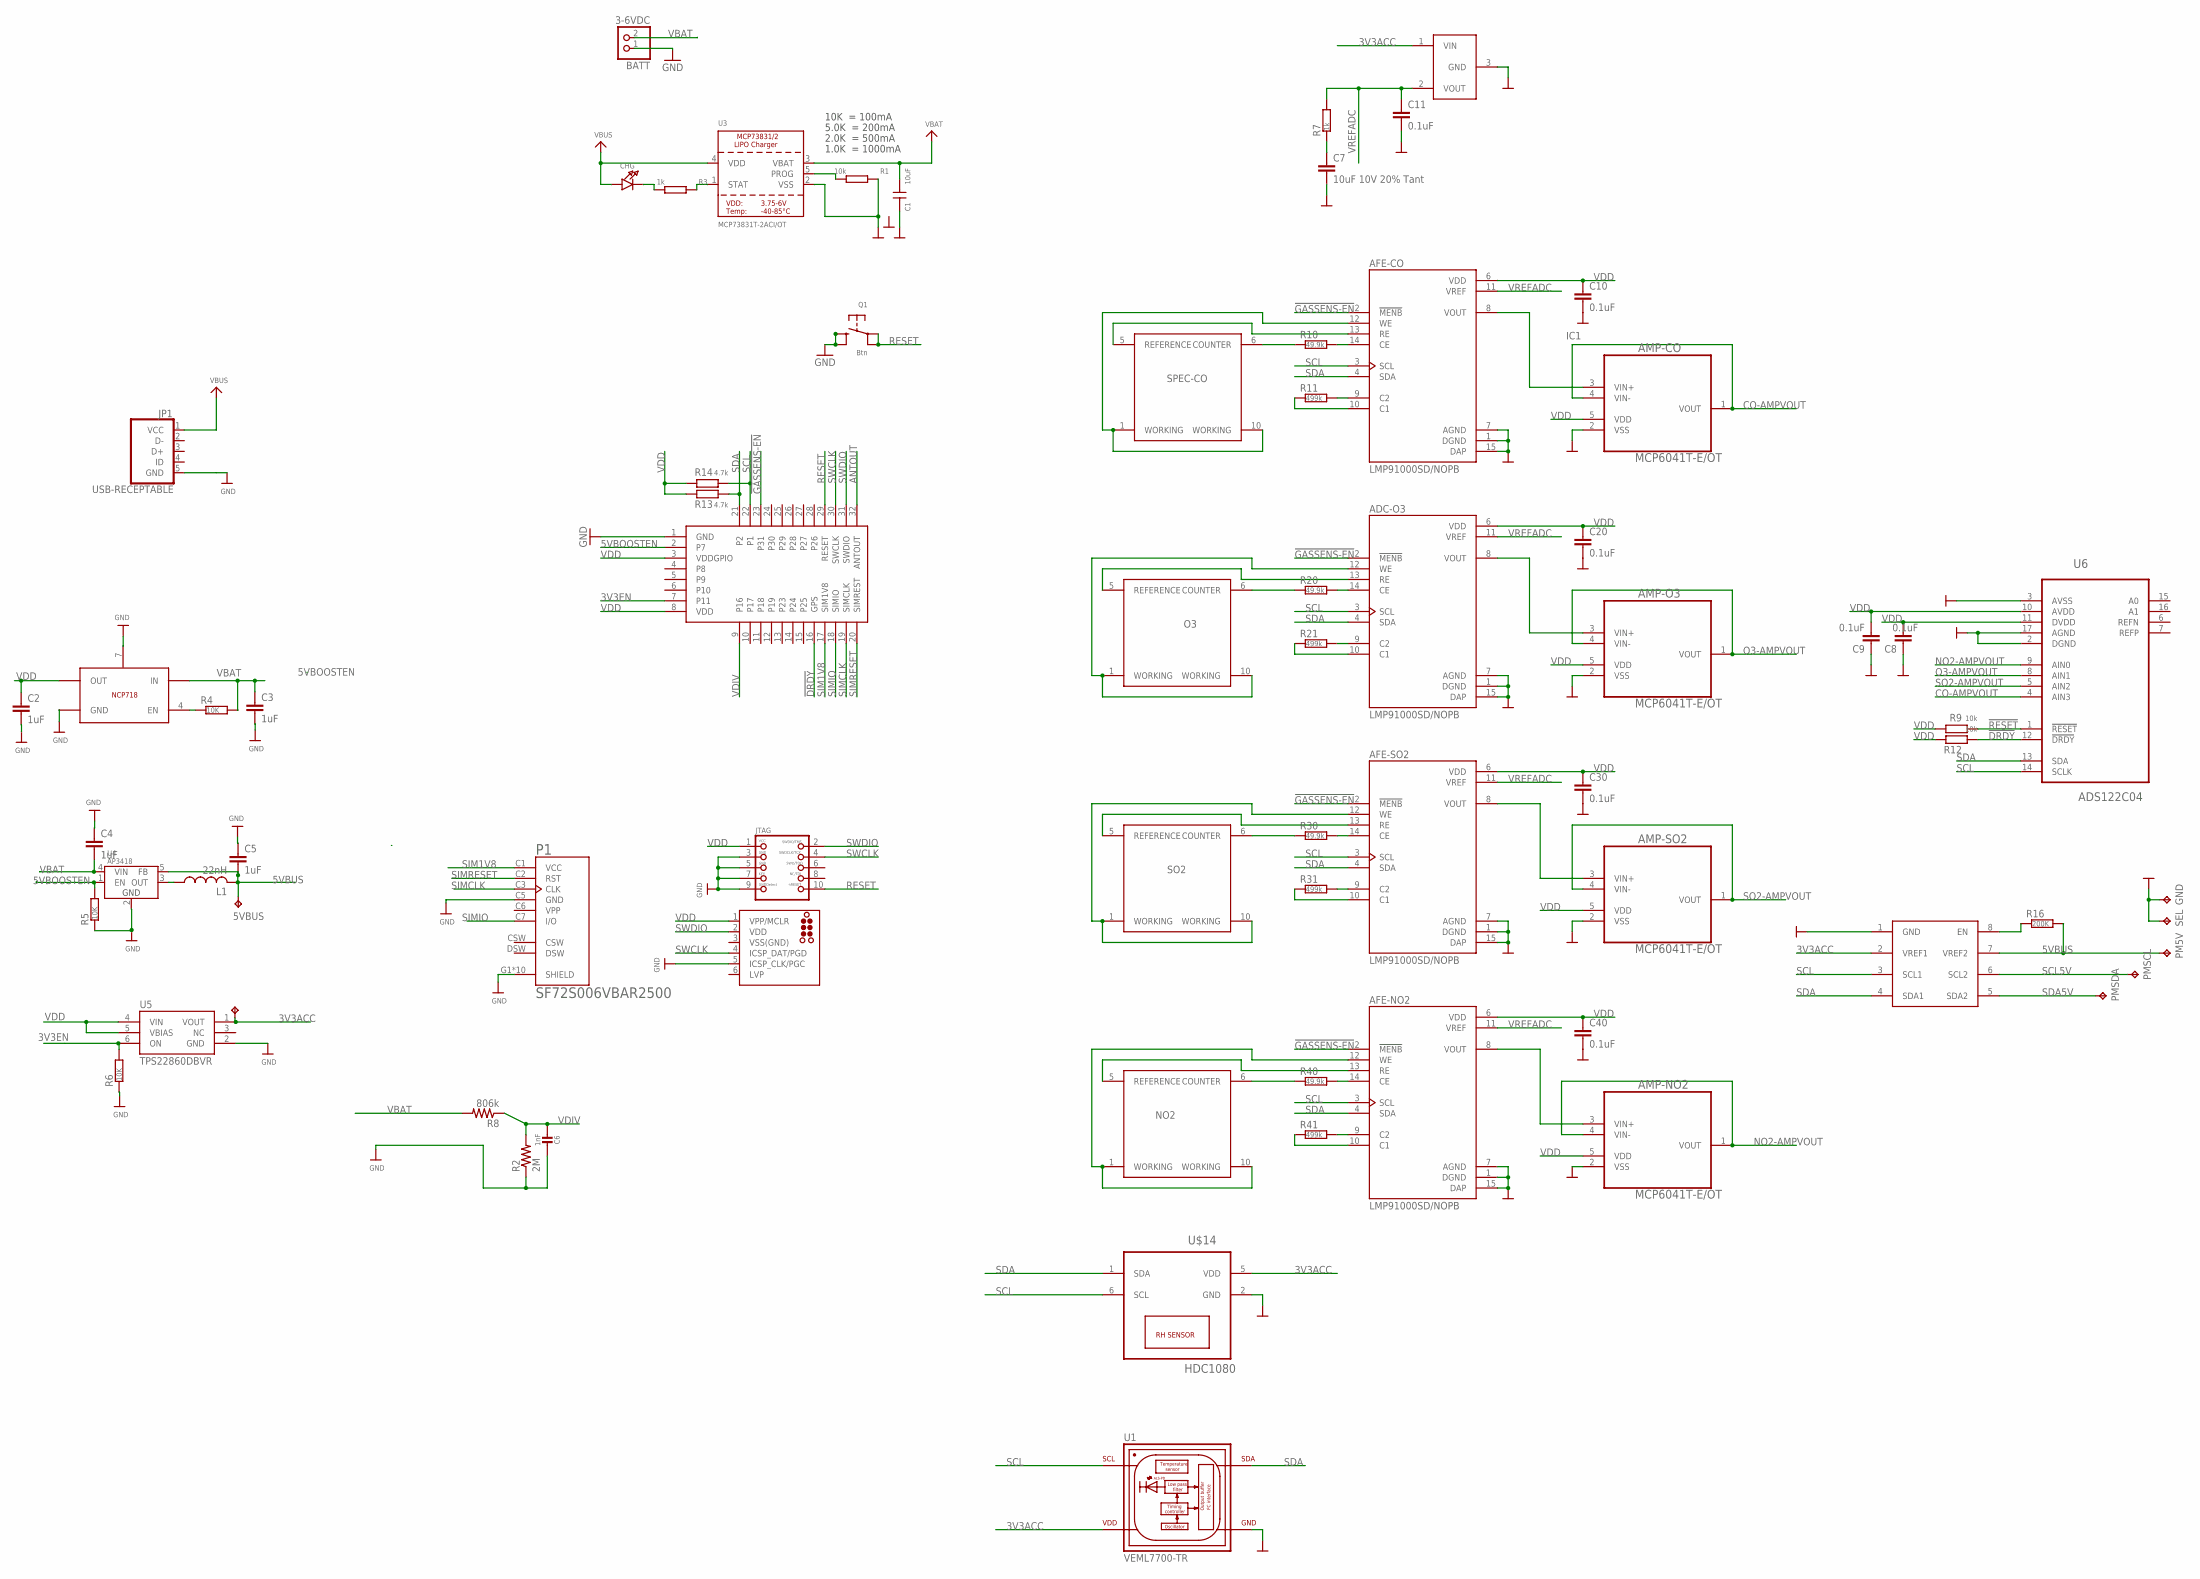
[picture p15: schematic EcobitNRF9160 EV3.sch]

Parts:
5VBUS, 5VBUS1: TPTP15R; TP15R
ADC-O3: LMP91000SD/NOPB; SON50P400X400X80-15N
AFE-CO: LMP91000SD/NOPB; SON50P400X400X80-15N
AFE-NO2: LMP91000SD/NOPB; SON50P400X400X80-15N
AFE-SO2: LMP91000SD/NOPB; SON50P400X400X80-15N
AMP-CO: MCP6041T-E/OT; SOT95P320X145-5N
AMP-NO2: MCP6041T-E/OT; SOT95P320X145-5N
AMP-O3: MCP6041T-E/OT; SOT95P320X145-5N
AMP-SO2: MCP6041T-E/OT; SOT95P320X145-5N
BATT: 3-6VDC; JSTPH2
C1: 10uF; C-0402
C2, C3, C4, C5: 1uF; RESC0402_N
C6: 1nF; 0603-NO
C7: 10uF 10V 20% Tant; RESC0805_N
C8, C9, C10, C11, C20, C30, C40: 0.1uF; RESC0603_N
CHG: LED0805_NOOUTLINE; CHIPLED_0805_NOOUTLINE
GND: TPTP15R; TP15R
IC1: ISL60002DIH320Z-TK; SOT-23-3
J2: TC2030-MCP-NL
JP1: USB-RECEPTABLE; FCI-10103594-0001LF
JTAG: JTAG-CORTEXM3; 2X05_1.27MM_SMT
L1: 22nH; RESC0603_N
P1: SF72S006VBAR2500; JAE_SF72S006VBAR2500
PM5V: TPTP15R; TP15R
PMSCL: TPTP15R; TP15R
PMSDA: TPTP15R; TP15R
Q1: Btn; BTN_KMR2_4.6X2.8
R1: 10k; R0402
R2: 2M; R0603
R3: 1k; R0402
R4, R5, R6: 10K; RESC0402_N
R7: 1k; RESC0603_N
R8: 806k; R0603
R9, R12: 10k; RESC0603_N
R10, R20, R30, R40: 49.9k; RESC0603_N
R11, R21, R31, R41: 499k; RESC0603_N
R13, R14: 4.7k; RESC0603_N
R16: 200K; RESC0402_N
SEL: TPTP15R; TP15R
SENS-CO: SPECSENSOR
SENS-NO2: SPECSENSOR
SENS-O3: SPECSENSOR
SENS-SO2: SPECSENSOR
U1: VEML7700-TR; XDCR_VEML7700-TR
U2: NCP718; NCP718-WDFN6
U3: MCP73831T-2ACI/OT; SOT23-5
U4: AP3418; SOT25
U5: TPS22860DBVR; R-PDSO-G6
U6: ADS122C04; QFN50P300X300X80-16N
U7: PCA9306; PSON35P135X100X50-8N
U$14: HDC1080; TI-S-PWSON-N6
U$35: NRF9160MODULE; NRF9160CASTALLATEDMODULE

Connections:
3V3ACC: 5VBUS1.TP, IC1.1 (VIN), U1.2 (VDD), U5.1 (VOUT), U7.2 (VREF1), U$14.5 (VDD)
3V3EN: R6.2, U5.6 (ON), U$35.7 (P11)
5VBOOSTEN: R5.2, U4.1 (EN), U$35.2 (P7)
5VBUS: 5VBUS.TP, C5.2, L1.2, PM5V.TP, R16.2, U4.5 (FB), U7.7 (VREF2)
!DRDY: R12.1, U6.12 (!DRDY), U$35.16 (GPS)
!GASSENS-EN: ADC-O3.2 (!MENB), AFE-CO.2 (!MENB), AFE-NO2.2 (!MENB), AFE-SO2.2 (!MENB), U$35.23 (P31)
!RESET: R9.1, U6.1 (!RESET)
ANTOUT: U$35.32 (ANTOUT)
CO-AMPVOUT: AMP-CO.1 (VOUT), AMP-CO.4 (VIN-), U6.4 (AIN3)
COVOUT: AFE-CO.8 (VOUT), AMP-CO.3 (VIN+)
GND: ADC-O3.1 (DGND), ADC-O3.7 (AGND), ADC-O3.15 (DAP), AFE-CO.1 (DGND), AFE-CO.7 (AGND), AFE-CO.15 (DAP), AFE-NO2.1 (DGND), AFE-NO2.7 (AGND), AFE-NO2.15 (DAP), AFE-SO2.1 (DGND), AFE-SO2.7 (AGND), AFE-SO2.15 (DAP), AMP-CO.2 (VSS), AMP-NO2.2 (VSS), AMP-O3.2 (VSS), AMP-SO2.2 (VSS), BATT.1, C1.2, C2.2, C3.2, C4.1, C5.1, C6.1, C7.2, C8.1, C9.1, C10.2, C11.2, C20.2, C30.2, C40.2, GND.TP, IC1.3 (GND), J2.5 (ICSP_CLK/PGC), JP1.5 (GND), JTAG.3, JTAG.5, JTAG.7, JTAG.9, P1.C5 (GND), P1.G1 (SHIELD), P1.G2 (SHIELD), P1.G3 (SHIELD), P1.G4 (SHIELD), P1.G5 (SHIELD), P1.G6 (SHIELD), P1.G7 (SHIELD), P1.G8 (SHIELD), P1.G9 (SHIELD), P1.G10 (SHIELD), Q1.B (S), Q1.B' (S1), R1.1, R2.1, R5.1, R6.1, SEL.TP, U1.3 (GND), U2.3 (GND), U2.7 (GND), U3.2 (VSS), U4.2 (GND), U5.2 (GND), U6.2 (DGND), U6.3 (AVSS), U6.17 (AGND), U7.1 (GND), U$14.2 (GND), U$35.1 (GND)
unnamed: R16.1, U7.8 (EN)
unnamed: L1.1, U4.3 (OUT)
unnamed: R3.1, U3.1 (STAT)
unnamed: CHG.C, R3.2
unnamed: AFE-CO.9 (C2), R11.2
unnamed: AFE-CO.10 (C1), R11.1
unnamed: R1.2, U3.5 (PROG)
unnamed: AFE-CO.14 (CE), R10.2
unnamed: C7.1, R7.1
unnamed: ADC-O3.9 (C2), R21.2
unnamed: ADC-O3.10 (C1), R21.1
unnamed: ADC-O3.14 (CE), R20.2
unnamed: AFE-SO2.9 (C2), R31.2
unnamed: AFE-SO2.10 (C1), R31.1
unnamed: AFE-SO2.14 (CE), R30.2
unnamed: AFE-NO2.9 (C2), R41.2
unnamed: AFE-NO2.10 (C1), R41.1
unnamed: AFE-NO2.14 (CE), R40.2
NO2-AMPVOUT: AMP-NO2.1 (VOUT), AMP-NO2.4 (VIN-), U6.9 (AIN0)
NO2VOUT: AFE-NO2.8 (VOUT), AMP-NO2.3 (VIN+)
O3-AMPVOUT: AMP-O3.1 (VOUT), AMP-O3.4 (VIN-), U6.8 (AIN1)
O3VOUT: ADC-O3.8 (VOUT), AMP-O3.3 (VIN+)
R-EN: R4.1, U2.4 (EN)
RESET: JTAG.10, Q1.A, Q1.A' (P1), U$35.29 (RESET)
SCL: ADC-O3.3 (SCL), AFE-CO.3 (SCL), AFE-NO2.3 (SCL), AFE-SO2.3 (SCL), R14.1, U1.1 (SCL), U6.14 (SCLK), U7.3 (SCL1), U$14.6 (SCL), U$35.22 (P1)
SCL5V: PMSCL.TP, U7.6 (SCL2)
SDA: ADC-O3.4 (SDA), AFE-CO.4 (SDA), AFE-NO2.4 (SDA), AFE-SO2.4 (SDA), R13.1, U1.4 (SDA), U6.13 (SDA), U7.4 (SDA1), U$14.1 (SDA), U$35.21 (P2)
SDA5V: PMSDA.TP, U7.5 (SDA2)
SIM1V8: P1.C1 (VCC), U$35.17 (SIM1V8)
SIMCLK: P1.C3 (CLK), U$35.19 (SIMCLK)
SIMIO: P1.C7 (I/O), U$35.18 (SIMIO)
SIMRESET: P1.C2 (RST), U$35.20 (SIMREST)
SO2-AMPVOUT: AMP-SO2.1 (VOUT), AMP-SO2.4 (VIN-), U6.5 (AIN2)
SO2VOUT: AFE-SO2.8 (VOUT), AMP-SO2.3 (VIN+)
SPEC-CO-COUNTER: R10.1, SENS-CO.6 (COUNTER)
SPEC-CO-REF: AFE-CO.13 (RE), SENS-CO.5 (REFERENCE)
SPEC-CO-WKG: AFE-CO.12 (WE), SENS-CO.1 (WORKING), SENS-CO.10 (WORKING)
SPEC-NO2-COUNTER: R40.1, SENS-NO2.6 (COUNTER)
SPEC-NO2-REF: AFE-NO2.13 (RE), SENS-NO2.5 (REFERENCE)
SPEC-NO2-WKG: AFE-NO2.12 (WE), SENS-NO2.1 (WORKING), SENS-NO2.10 (WORKING)
SPEC-O3-COUNTER: R20.1, SENS-O3.6 (COUNTER)
SPEC-O3-REF: ADC-O3.13 (RE), SENS-O3.5 (REFERENCE)
SPEC-O3-WKG: ADC-O3.12 (WE), SENS-O3.1 (WORKING), SENS-O3.10 (WORKING)
SPEC-SO2-COUNTER: R30.1, SENS-SO2.6 (COUNTER)
SPEC-SO2-REF: AFE-SO2.13 (RE), SENS-SO2.5 (REFERENCE)
SPEC-SO2-WKG: AFE-SO2.12 (WE), SENS-SO2.1 (WORKING), SENS-SO2.10 (WORKING)
SWCLK: J2.4 (ICSP_DAT/PGD), JTAG.4, U$35.30 (SWCLK)
SWDIO: J2.2 (VDD), JTAG.2, U$35.31 (SWDIO)
VBAT: BATT.2, C1.1, C3.1, C4.2, R4.2, R8.2, U2.6 (IN), U3.3 (VBAT), U4.4 (VIN)
VBUS: CHG.A, JP1.1 (VCC), U3.4 (VDD)
VDD: ADC-O3.6 (VDD), AFE-CO.6 (VDD), AFE-NO2.6 (VDD), AFE-SO2.6 (VDD), AMP-CO.5 (VDD), AMP-NO2.5 (VDD), AMP-O3.5 (VDD), AMP-SO2.5 (VDD), C2.1, C8.2, C9.2, C10.1, C20.1, C30.1, C40.1, J2.1 (VPP/MCLR), JTAG.1, R9.2, R12.2, R13.2, R14.2, U2.1 (OUT), U5.4 (VIN), U5.5 (VBIAS), U6.10 (AVDD), U6.11 (DVDD), U$35.3 (VDDGPIO), U$35.8 (VDD)
VDIV: C6.2, R2.2, R8.1, U$35.9 (P16)
VPP: P1.C6 (VPP)
VREFADC: ADC-O3.11 (VREF), AFE-CO.11 (VREF), AFE-NO2.11 (VREF), AFE-SO2.11 (VREF), C11.1, IC1.2 (VOUT), R7.2
VSS(GND): J2.3 (VSS(GND))

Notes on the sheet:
10K = 100mA
5.0K = 200mA
2.0K = 500mA
1.0K = 1000mA

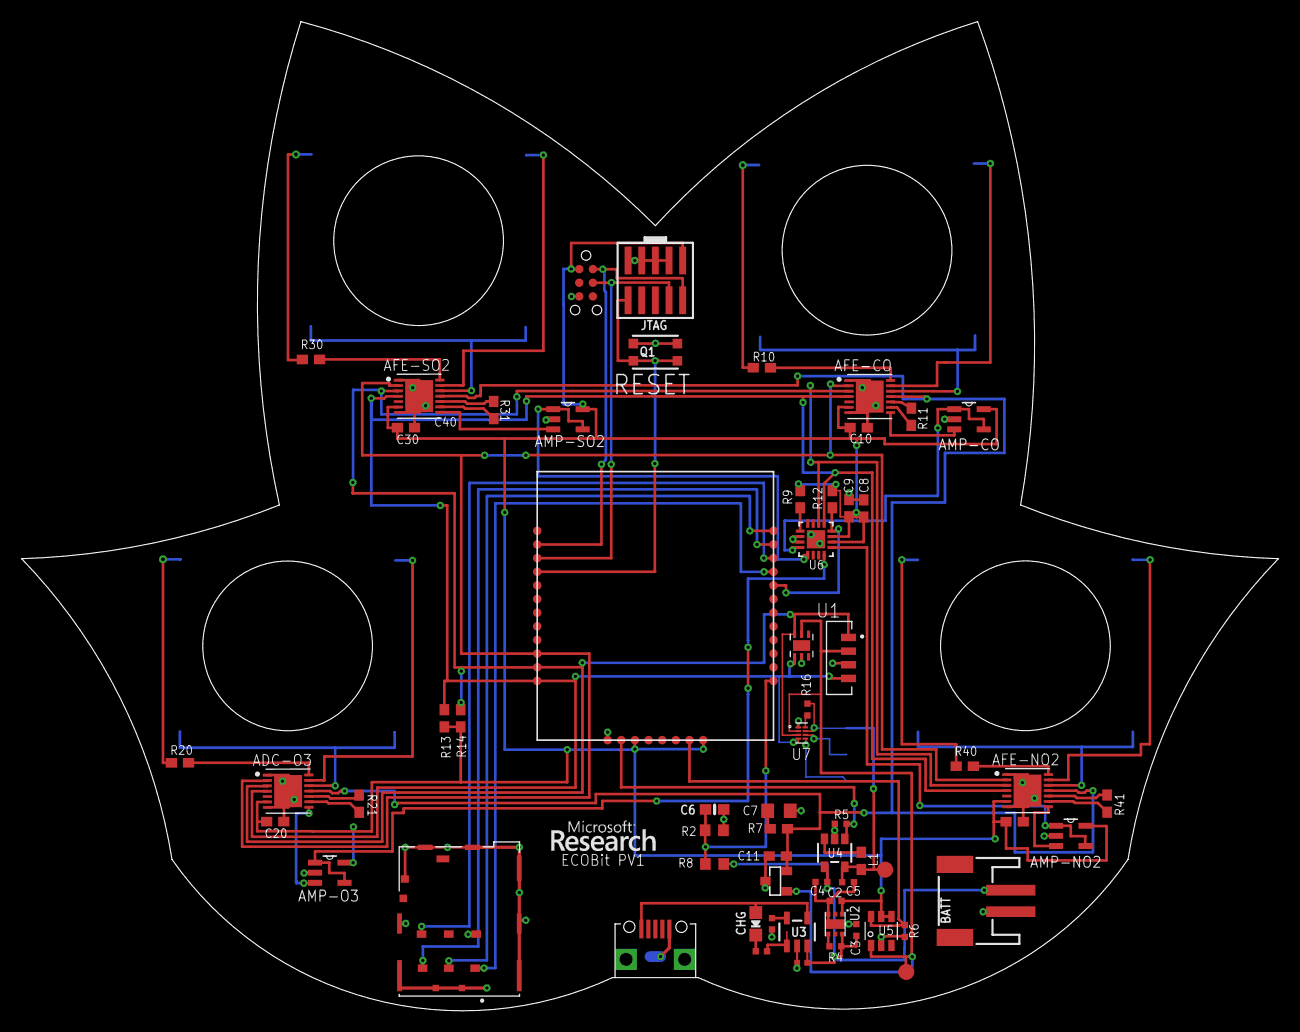
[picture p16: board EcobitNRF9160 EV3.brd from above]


Board: 2 copper layers, 117.0 x 92.1 mm, 72 parts (9 on the bottom side), 63 nets.

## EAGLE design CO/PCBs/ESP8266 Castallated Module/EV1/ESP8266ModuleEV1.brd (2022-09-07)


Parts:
C1, C3: 0.1uF; RESC0402_N
C2: 10uF; RESC0402_N
IC1: ESP-WROOM-02
LED: LED0603; LED-0603
Q1, Q2: Btn; BTN_KMR2_4.6X2.8
R1, R4: 1k; R0402
R2: 10k; RESC0402_N
R3, R5, R6: 10k; R0402
U$5: 1X8HEADER; 8X1
U$10, U$11: 1X12HEADER; 1X12

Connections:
3V3EN: IC1.10 (IO4), U$5.2
5VBOOSTEN: IC1.4 (IO12), U$5.7
!GASENABLE: IC1.5 (IO13), U$10.10
GND: C1.2, C2.2, C3.2, IC1.9 (GND1), IC1.13 (GND2), IC1.18 (GND3), IC1.19 (GND0), LED.C, Q1.B (S), Q1.B' (S1), Q2.B (S), Q2.B' (S1), U$5.8
LED: IC1.17 (IO16), R1.2
unnamed: C3.1, IC1.2 (EN), R2.2
unnamed: IC1.6 (IO15), R6.1
unnamed: Q2.A, Q2.A' (P1), R4.2
unnamed: LED.A, R1.1
P8: U$5.5
P9: U$5.4
P10: U$5.3
P17: U$11.2
P18: U$11.3
P19: U$11.4
P23: U$11.5
P24: U$11.6
P29: U$10.8
PGM: IC1.8 (IO0), R3.1, R4.1
RESET: IC1.15 (RST), Q1.A, Q1.A' (P1), R5.2
RX: IC1.11 (RXD)
SCL: IC1.3 (IO14), U$10.11
SDA: IC1.7 (IO2), U$10.12
SIM1V8: U$11.9
TX: IC1.12 (TXD)
VDD: C1.1, C2.1, IC1.1 (3V3), R2.1, R3.2, R5.1, R6.2, U$5.1
VDIV: IC1.16 (TOUT), U$11.1


Board: 2 copper layers, 25.2 x 22.0 mm, 16 parts (0 on the bottom side), 15 nets.

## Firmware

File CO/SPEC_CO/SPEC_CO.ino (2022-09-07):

#include "SPEC_CO.h"

void setup() {
  Serial.begin(9600);
  Serial.println("-----PROGRAM START-----");
  Serial.println("Zeroing CO sensor...");

  zeroSensor(10);
  
  Serial.print("voffset = ");
  Serial.print(voffset);
  Serial.print(" mV");
  Serial.println();
  
  Serial.print("tzero = ");
  Serial.print(tzero);
  Serial.print(" degrees C");
  Serial.println();

  pinMode(LED_BUILTIN, OUTPUT);
}

void loop() {
  float conc = getConcentration(5);
  //convertX('B');
  digitalWrite(LED_BUILTIN, HIGH);
  delay(500);
  digitalWrite(LED_BUILTIN, LOW);
  delay(500);
  Serial.print(conc);
  Serial.println("ppm.");
}

float zeroSensor(int duration) {
  unsigned long startMillis;
  unsigned long durationMs = duration * 1000;
  unsigned long gasSum = 0;//, tempSum = 0;
  unsigned int i = 0;
  
  float tempSum = 0, ran = random(36800, 36850) / 100.0;
  startMillis = millis();
  do {
    gasSum += analogRead(vgasPin);
    tempSum += ran;
    i++;
    delay(1);
  } while((millis() - startMillis) < durationMs);

  float gasAvg = (float)gasSum / (float)i;
  float vgas = gasAvg * Vcc * 1000.0 / 1024.0;
  Serial.print("gasAvg: ");
  Serial.println(gasAvg);
  Serial.print("vgas: ");
  Serial.println(vgas);
  Serial.print("Vref: ");
  Serial.println(Vref);
  Serial.print("voffset: ");
  Serial.println(voffset);
  voffset = vgas - Vref;

  float tempAvg = (float)tempSum / (float)i;
  float vtemp = tempAvg * Vcc / 1024.0;
  tzero = (Tspan / Vsup) * vtemp - Toffset;

  return voffset;
}

float getConcentration(int duration) {
  unsigned long startMillis;
  unsigned long durationMs = duration * 1000;
  unsigned long gasSum = 0; //, tempSum = 0;
  unsigned int i = 0;

  float tempSum = 0, ran = random(37000, 37200) / 100.0;
  startMillis = millis();
  do {
    gasSum += analogRead(vgasPin);
    tempSum += ran; // analogRead(vtempPin);
    i++;
    delay(1);
  } while((millis() - startMillis) < durationMs);

  float gasAvg = (float)gasSum / (float)i;
  float vgas = gasAvg * Vcc * 1000.0 / 1024.0;

  float tempAvg = (float)tempSum / (float)i;
  float vtemp = tempAvg * Vcc / 1024.0;
  float temp = (Tspan / Vsup) * vtemp - Toffset;
  Serial.print("Vref:");
  Serial.println(Vref);
  Serial.print("Voffset:");
  Serial.println(voffset);
  float nA = (vgas - Vref - voffset) / (float)CO_TIA_GAIN * 1000000.0;

  //temperature compensation
  if (temp > 23.0) {
    nA -= O3_A_HI * (temp - tzero);
  } else {
    nA -= O3_A_LO * (temp - tzero);
  }

  return nA / SENS_CODE * (1 - CO_TEMP_C * (temp - tzero));
}

float convertX(char U){
  float pX = 0;
  if (U == 'B')  return pX;
  else if (U == 'M') return (pX/1000.0);
  else return 0;
}

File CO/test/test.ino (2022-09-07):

/*
 * main.cpp
 * Kaveh Pezeshki 6/22/2021
 * Ozone sensor controller (ULPSM-O3) using a Teensy
 */

#define SENS_CODE 4.19 // sensitivity code
#define GAIN 100000      // TIA gain (kV/A)

#define VGAS_PIN A2
#define VREF_PIN A1
#define VREG A0

float vgas0 = 0;       // voltage output gas signal in clean-air environment


float voltageToConc(float voltage) {
    // the calibration here is specified in datasheet ULPSM-O3 968-046

    float M = ((float)SENS_CODE) * ((float)GAIN) * 1e-6;
    float conc = (1/M) * (voltage - vgas0);

    return conc;
}

float readConc() {
    // measures differential voltage between Vgas and Vref, returns output voltage
    // datasheet recommends buffer here

    int inVoltage = analogRead(VGAS_PIN) - 512; // analogRead(VREF_PIN);

    //Serial.print("inVoltage "); Serial.println(inVoltage);

    float diffVoltage = ((float) inVoltage) * 3.3 / 1024.0;

    //Serial.print("diffVoltage "); Serial.println(diffVoltage);

    return voltageToConc(diffVoltage);
}

void setup() {
    Serial.begin(115200);
    Serial.println("ULPSM-O3 Driver");
    
    double buf;
    int numsamples;

    for (int i = 0; i < 1000; i++) {
      buf += analogRead(VGAS_PIN) - 512;
      numsamples += 1;
      delay(1);
    }

    vgas0 = (buf / ((float) numsamples)) * 3.3/1024.0;

}

void loop() {

    double buf;
    int numsamples;

    for (int i = 0; i < 1000; i++) {
      buf += readConc();
      numsamples += 1;
      delay(1);
    }

    double conc = buf / numsamples;

    //char concChar[10];
    //dtostre(conc, concChar, 3, 0);

    Serial.print("Derived concentration ");
    Serial.println(conc);

    //Serial.print("temperature ");
    //Serial.println(analogRead(VTEMP_PIN));

    Serial.println();

}

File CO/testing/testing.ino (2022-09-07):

#define SENSITIVITY_CODE  4.46
#define TIA_GAIN  100000
#define FIXED_GAIN   pow(10,-6)
//#define SENSOR_CALIBRATION_FACTOR SENSITIVITY_CODE*TIA_GAIN*FIXED_GAIN
//#define GAS_CONCENTRATION (1/SENSOR_CALIBRATION_FACTOR)*(Vgas-Vref)

float Vreg;
float Vref;
float Vgas;
float V5;

void setup() {
  // put your setup code here, to run once:
  Serial.begin(9600);
  Vreg = analogRead(A0);
  Vref = analogRead(A1);
  Vreg = Vreg / 1024 * 5;
  Vref = Vref / 1024 * 5;
  
  V5 = analogRead(A3);
  Serial.print("Vreg: ");
  Serial.println(Vreg);
  //Serial.println(Vreg/675.84*3.3);
  Serial.print("Vref: ");
  Serial.println(Vref);
  Serial.print("V5: ");
  Serial.println(V5);
}
float concentration(){
  Vgas = analogRead(A2);
  //Serial.println(Vgas);
  Vgas = Vgas / 1024 * 5;
  //Serial.println(Vgas);

  //float Vgas0 = ( Vreg * float(2000 + 1000000) ) / ( float(2000 + 2000000) * 1000.0 )
  //Serial.print("Vgas-Vref: ");
  //Serial.println(Vgas-Vref);
  float SENSOR_CALIBRATION_FACTOR = SENSITIVITY_CODE * TIA_GAIN * FIXED_GAIN;
  Serial.println(SENSOR_CALIBRATION_FACTOR);
  float GAS_CONCENTRATION = (1/SENSOR_CALIBRATION_FACTOR)*(Vgas-Vref);
  Serial.println(GAS_CONCENTRATION);
  return (float)GAS_CONCENTRATION*1000;

}
//void loop(){}
void loop() {
  // put your main code here, to run repeatedly:
  static int count = 0;
  float ppm = concentration();

  // Serial.println("Vreg: " + String(Vreg));
  // Serial.println("Vref: " + String(Vref));
  // Serial.println("Vgas: " + String(Vgas));
  Serial.print(count++);
  Serial.print(": ");
  Serial.print((int)ppm);
  Serial.println(" ppb.");

  delay(2000);

}

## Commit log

2022-07-28 CO Sensor PCB Design
    [EcobitNRF9160 EV3-B_Cu.gbl, EcobitNRF9160 EV3-B_Paste.gbp, EcobitNRF9160 EV3-Edge_Cuts.gm1, EcobitNRF9160 EV3-F_Cu.gtl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]
2022-08-03 New CO PCB Design
    [ULPSM_R12.kicad_pcb, ULPSM_R12.kicad_sch]
2022-08-03 new pcb design for CO
2022-08-03 NEW PCB DESIGN

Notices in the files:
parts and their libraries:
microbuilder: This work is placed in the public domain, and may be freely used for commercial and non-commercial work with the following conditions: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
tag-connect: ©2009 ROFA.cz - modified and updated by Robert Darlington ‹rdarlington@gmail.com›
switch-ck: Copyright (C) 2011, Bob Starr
